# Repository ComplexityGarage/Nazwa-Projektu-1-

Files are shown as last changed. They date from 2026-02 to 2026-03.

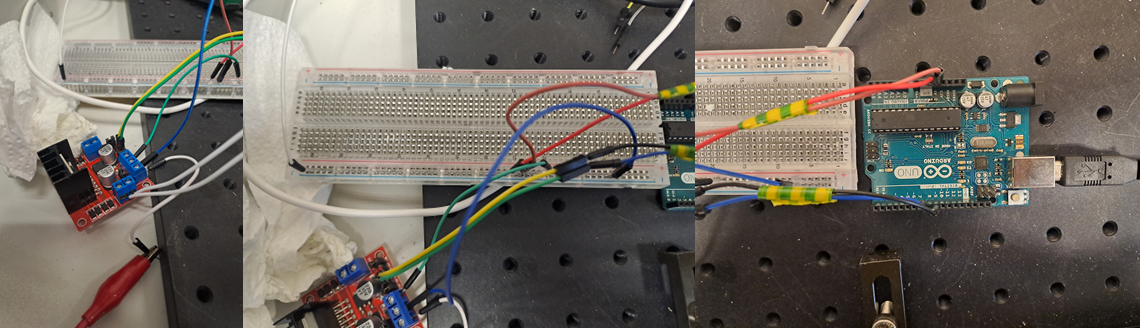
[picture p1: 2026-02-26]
123.png

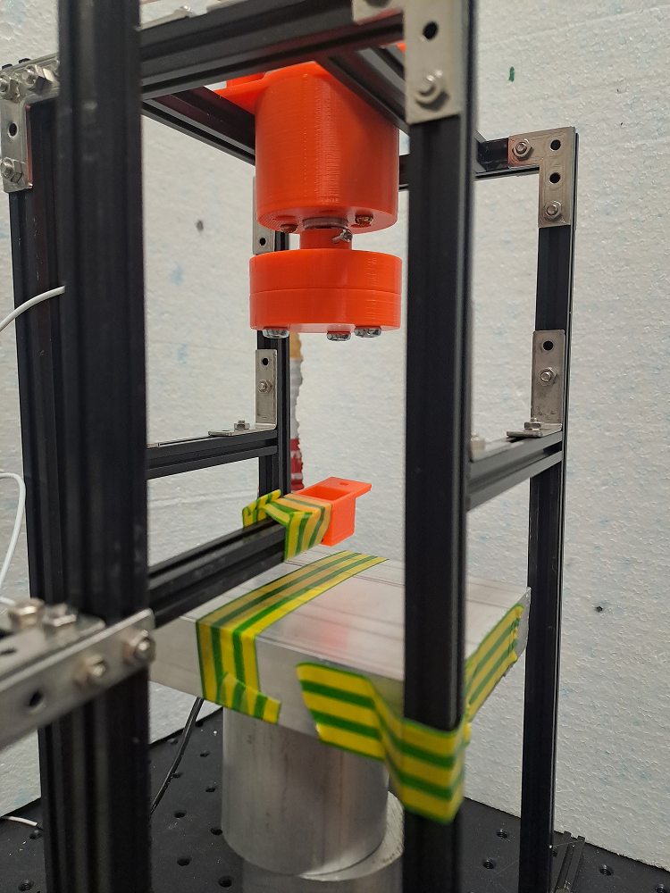
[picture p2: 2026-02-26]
20260213_160208.png

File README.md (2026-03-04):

# PFR-magnetic-levitation

Polarity free repulsion (PFR) is a magnetic levitation technique in which one magnet (rotor) is spun around its axis at ~200Hz, and a second magnet (floater) levitates underneath it. One of the main challenges of achieving levitation is placing the floater in the minimum of the potential. Quite often, the floater is immediately ejected, without ever levitating. The main goal of this project is to create a system that can reliably insert the floater in the minimum of the potential, where it can levitate. 

# Tech used

- NdFeB magnets, nickel coated, 1x1x1 cm, 6.3kg holding power
- 12V DC motor
- Arduino Uno
- HW-095 motor driver
- GY-271 QMC5883L magnetometer
- KA3005P programmable DC power supply (30V)

# Setup (levitation)

The setup can be seen in the images below. The motor itself is held by a 3D printed holder. The holder is connected to aluminium frames, which dampen vibrations of the motor. This is essential for stable levitation. The motor rotates at a constant frequency, and is controlled via the HW-095 motor driver. The motor driver is connected to a programmable power supply and arduino. The arduino determines whether the motor is on, and the motor speed scales linearly with voltage on the power supply. ...cm under the motor there is an aluminium plate of dimensions (8,8 x 10,2 x 2 cm), which help stabilize the floater via eddy currents.





# 3D Component Design
The magnet box consists of two parts. The upper part attaches the entire assembly to the motor and features two symmetrically placed screw holes on either side of the bracket. Inside, there is a slot for a $10 \times 10 \times 10 \text{ mm}$ cubic magnet, rotated by 10°. After placing the magnet inside, the entire assembly is secured with three screws.

Box

The second box was designed for automatic magnet positioning. Once the stability point is found, it should be lowered, leaving the magnet in a state of levitation. The motor holder features ventilation holes and two screw holes matched to the specific motor being used. It is secured from the top with four screws.



# Setup (Insertion system)

The ideal insertion system would be a robot arm, automated to follow a specific path to place the floater in the right spot. We ordered a simple robot arm based on arduino servomotors. However, we saw that the movement axes of the arm were not cartesian, which would make it difficult to find a good path. Furthermore, the arm was not that stable, meaning that it could be unreliable. So given the time constraints, we decided to go for a manually controlled arm, made from aluminium frames. This has potential advantages. The axes are cartesian, making the movements of the arm more intuitive. Also, if there are changes in the system (such as a different motor speed), it is easier to adapt using a manual arm. With a fully automated arm, new tests may have to be done to find the new equilibrium position.
The manual system is shown in the figure below. There are two vertical aluminium frames, which act like the vertical axis. Between these is a short horizontal frame, which acts as the horizontal axis. This horizontal frame can be moved up and down, as the bolts are just loose enough to allow for movement, but tight enough to prevent it from falling. Parallel to the horizontal axis is a longer frame. This arm is attached in two points to the shorter frame, also with loose bolts. This allows for horizontal movement of the arm. 



By attaching the a magnet holder to the end of the arm, it should be possible to levitate the magnet without moving your hands close to the motor.

# Magnetic field measurements
We studied the shape of the magnetic field with the hope to discover the potential minimum. We used the GY-271 magnetometer, which measures all three cartesian components. The z-component is vertical. First we used the weaker magnets as a rotor, and then the stronger ones. The results are presented below. The values are not calibrated, but we assume a monotonous relation between the units of the magnetometer and the magnetic field strength, and a zero bias value. Then the location of the minima, maxima and the point where B=0 are accurately represented by this data. It is of course a very rough analysis, so further research is needed to determine the accuracy of our results, and how it relates exactly to the equilibrium position of the floater. 




=

The graphs above show the magnetic field strength, in the units of the magnetometer, as a function of height difference between rotor and floater. This was done for the weaker of the two magnets. THis was done for different horizontal offsets b from the rotor axis. As can be seen, for most values of b, there is a clear relation between h and m. It is interesting to note the differences between the x and y graphs, as it means that there is some sort of symmetry breaking.






These graphs show the height-magnetic field strength relation for the stronger rotor magnet. Here, the different colors do not indicate horizontal offset, but the voltage applied over the motor (which is proportional to the motor speed). We do not see a significant difference between 9V and 10V.

# Levitation attempts
We did not manage to achieve levitation. However, we now think that we might have oriented the rotor magnet incorrectly, as its poles should probably be horizontal and not vertical.

# Authors

Witold Kamphorst

Paulina Skalik

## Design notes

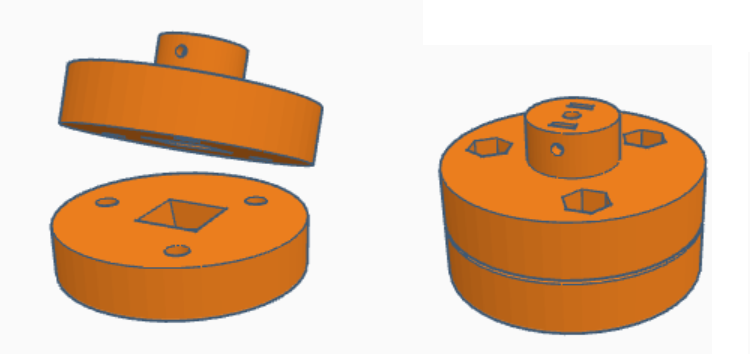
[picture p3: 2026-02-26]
Box .png

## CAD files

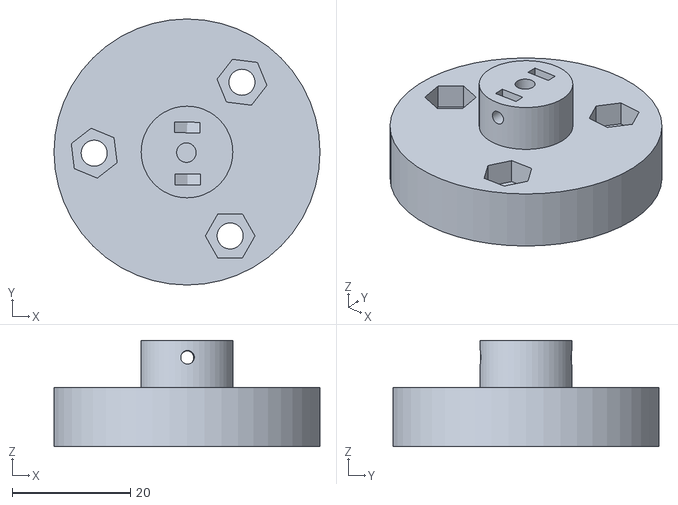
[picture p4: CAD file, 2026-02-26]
stl/Box project 1.stl
45.0 x 45.0 x 17.9

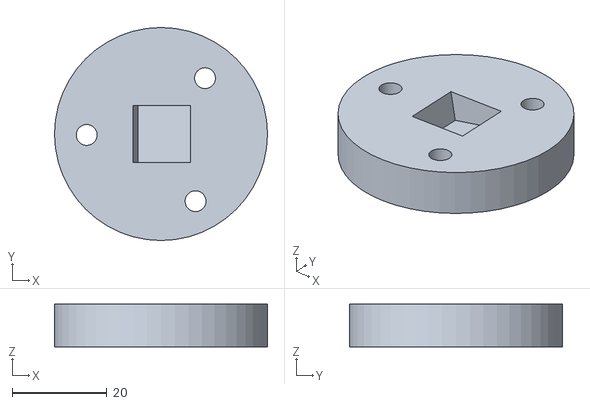
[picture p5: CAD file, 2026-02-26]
stl/Box project 2.stl
45.0 x 45.0 x 9.00

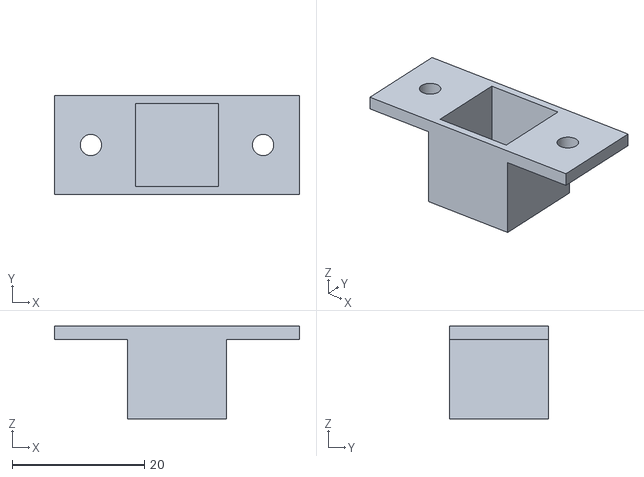
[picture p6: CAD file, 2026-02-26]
stl/Magnet Box.stl
37.0 x 15.0 x 14.0

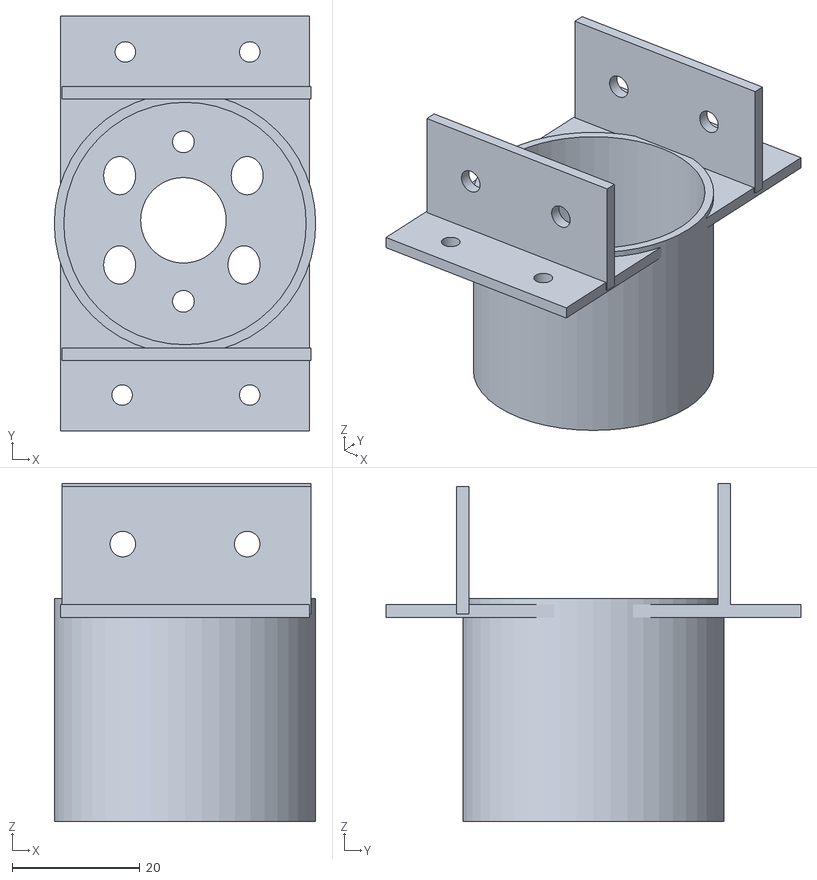
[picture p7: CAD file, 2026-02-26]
stl/Motor holder.stl
41.0 x 65.0 x 53.0
